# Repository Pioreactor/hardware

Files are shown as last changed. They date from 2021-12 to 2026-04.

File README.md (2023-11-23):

### HAT hardware setup

#### Installation

0. Install git: `sudo apt-get install git -y`
1. git clone this repo to your Raspberry Pi: `git clone --recurse-submodules https://github.com/Pioreactor/hardware.git && cd hardware`
2. Install eeprom utils: `cd hats/eepromutils && make && sudo make install && cd ..`
3. Move some files over: `mv ../eeprom/write_eeprom.py eepromutils/ && mv ../eeprom/pioreactor_eeprom_settings.txt.template eepromutils/`

#### Setting up a new HAT

0. Attach the HAT to the RPi.
1. Run `sudo bash setup_HAT.py`
2. Record the serial number/UUID
2. After a `sudo reboot`, try  `pio version -v` to confirm that HATs version.

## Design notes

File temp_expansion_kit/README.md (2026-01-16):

# Temperature Expansion Kit

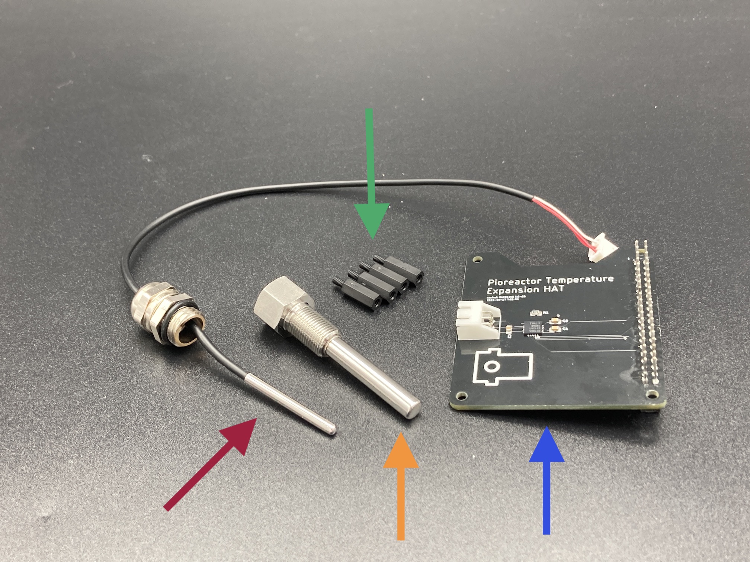
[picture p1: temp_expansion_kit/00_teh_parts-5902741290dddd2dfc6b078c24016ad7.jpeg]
Temperature Expansion Kit parts


### Pt1000 probe and cable

Need a 3-wire Pt1000 probe with jst connector. 

We Purchased from [here](https://www.alibaba.com/product-detail/GAIMC-Customized-waterproof-ClassA-PT1000-PT100_1600338752153.html?spm=a2756.trade-list-buyer.0.0.289276e9jdTwxA) 

 - 5mm diameter 47mm length hot sleeve with g1/8 threads
 - 3mm diameter probe

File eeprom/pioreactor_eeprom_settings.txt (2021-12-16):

########################################################################
# EEPROM settings text file
#
# Edit this file for your particular board and run through eepmake tool,
# then use eepflash tool to write to attached HAT ID EEPROM
#
# Tools available:
#  eepmake   Parses EEPROM text file and creates binary .eep file
#  eepdump   Dumps a binary .eep file as human readable text (for debug)
#  eepflash  Write or read .eep binary image to/from HAT EEPROM
#
########################################################################

########################################################################
# Vendor info

# 128 bit UUID. If left at zero eepmake tool will auto-generate
# RFC 4122 compliant UUID
product_uuid 00000000-0000-0000-0000-000000000000

# 16 bit product id
product_id 0x0001

# 16 bit product version
product_ver 0x0021

# ASCII vendor string  (max 255 characters)
vendor "Pioreactor Inc."

# ASCII product string (max 255 characters)
product "Pioreactor HAT"

# Custom binary data
2021-12-15T23:16:09.684411
########################################################################
# GPIO bank settings, set to nonzero to change from the default.
# NOTE these setting can only be set per BANK, uncommenting any of
# these will force the bank to use the custom setting.

# drive strength, 0=default, 1-8=2,4,6,8,10,12,14,16mA, 9-15=reserved
gpio_drive 0

# 0=default, 1=slew rate limiting, 2=no slew limiting, 3=reserved
gpio_slew 0

# 0=default, 1=hysteresis disabled, 2=hysteresis enabled, 3=reserved
gpio_hysteresis 0

# If board back-powers Pi via 5V GPIO header pins:
# 0 = board does not back-power
# 1 = board back-powers and can supply the Pi with a minimum of 1.3A
# 2 = board back-powers and can supply the Pi with a minimum of 2A
# 3 = reserved
# If back_power=2 then USB high current mode will be automatically
# enabled on the Pi
back_power 0

########################################################################
# GPIO pins, uncomment for GPIOs used on board
# Options for FUNCTION: INPUT, OUTPUT, ALT0-ALT5
# Options for PULL: DEFAULT, UP, DOWN, NONE
# NB GPIO0 and GPIO1 are reserved for ID EEPROM so cannot be set

#         GPIO  FUNCTION  PULL
#         ----  --------  ----
#setgpio  2     INPUT     DEFAULT
#setgpio  3     INPUT     DEFAULT
#setgpio  4     INPUT     DEFAULT
#setgpio  5     INPUT     DEFAULT
#setgpio  6     INPUT     DEFAULT
#setgpio  7     INPUT     DEFAULT
#setgpio  8     INPUT     DEFAULT
#setgpio  9     INPUT     DEFAULT
#setgpio  10    INPUT     DEFAULT
#setgpio  11    INPUT     DEFAULT
setgpio  12    OUTPUT     DEFAULT
setgpio  13    OUTPUT     DEFAULT
#setgpio  14    INPUT     DEFAULT
#setgpio  15    INPUT     DEFAULT
setgpio  16    OUTPUT     DEFAULT
setgpio  17    OUTPUT     DEFAULT
setgpio  18    OUTPUT     DEFAULT
#setgpio  19    INPUT     DEFAULT
#setgpio  20    INPUT     DEFAULT
#setgpio  21    INPUT     DEFAULT
#setgpio  22    INPUT     DEFAULT
setgpio  23    OUTPUT     DEFAULT
setgpio  24    INPUT     DEFAULT
setgpio  25    INPUT     DEFAULT
#setgpio  26    INPUT     DEFAULT
#setgpio  27    INPUT     DEFAULT

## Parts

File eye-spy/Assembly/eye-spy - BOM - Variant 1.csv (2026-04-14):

Reference | Qty | Description | Value | Manufacturer 1 | Manufacturer Part Number 1
C1 | 1 | CAP CER 10000PF 100V C0G 1206 | 10nF | Murata Electronics | GCM3195C2A103JA16D
C2,C4 | 2 | CAP CER 0.1UF 50V X7R 0402 | 0.1 uF | Murata Electronics | GRM155R71H104KE14J
C3 | 1 | CAP CER 1UF 50V X7R 1206 | 1uF | Murata Electronics | GRM31CR71H105KA61L
C5 | 1 | CAP TANT 10UF 10% 16V 1206 | 10uF | KYOCERA AVX | TAJA106K016RNJ
D1 | 1 | SENSOR PHOTODIODE 940NM 2SMD | VEMD2000X01 | Vishay Semiconductor | VEMD2000X01
D2,D3,D4,D5 | 4 | TVS DIODE 5V 15V SOD923 | DF2S6.8MFS,L3M | Toshiba | DF2S6.8MFS,L3M
J1,J2 | 2 | CONN HEADER SMD 4POS 1MM | BM04B-SRSS-TB | JST Sales America Inc. | BM04B-SRSS-TB
PCB1 | 1 | PCB | 3_20250920
R1 | 1 | RES 3.01M OHM 1% 1/16W 0402 | 3.01M | Yageo | RC0402FR-073M01L
R2,R4,R5,R6 | 4 | RES SMD 49.9 OHM 1% 1/16W 0402 | 49.9R | Yageo | RC0402FR-0749R9L
R3,R7 | 2 | RES 47K OHM 1% 1/16W 0402 | 47k | Yageo | RC0402FR-0747KL
U1 | 1 | IC OPAMP GP 1 CIRCUIT SC70-5 | TLV9101IDCK | Texas Instruments | TLV9101IDCK
U2 | 1 | IC ADC 16BIT SIGMA-DELTA 10VSSOP | ADS1114IDGS | Texas Instruments | ADS1114IDGSR

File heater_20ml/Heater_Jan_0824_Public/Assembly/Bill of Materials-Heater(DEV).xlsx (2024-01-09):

Designator | Value | Description | Manufacturer 1 | Manufacturer Part Number 1 | Supplier 1 | Supplier Part Number 1 | Supplier Unit Price 1 | Quantity | Supplier Subtotal 1
C1, C3 | 2.2uF | CAP CER 2.2UF 25V X5R 0603 | Murata | GRM188R61E225MA12D | Digi-Key | 490-12738-1-ND | 0.13 | 2 | 0.26
C2, C4 | 0.1uF | CAP CER 0.1UF 50V X7R 0402 | Murata | GRM155R71H104KE14J | Digi-Key | 490-13342-1-ND | 0.1 | 2 | 0.2
J1 | 0522070760 | CONN FFC FPC TOP 7POS 1.00MM R/A | Molex | 52207-0760 | Digi-Key | WM3818TR-ND |  | 1
MTL1, MTL2 | 9774030151R | RND STANDOFF M2.5X0.45 STEEL 3MM | Wurth Electronics | 9774030151R | Digi-Key | 732-7083-1-ND | 1.01 | 2 | 2.02
PCB1 | 4_20221023_001 |  |  |  |  |  |  | 1
R9 | 10k | RES SMD 10K OHM 1% 1/16W 0402 | Yageo | RC0402FR-0710KL | Digi-Key | 311-10.0KLRCT-ND | 0.1 | 1 | 0.1
R12, R13, R14, R16, R17, R19, R20, R21, R22, R23, R24, R25, R26, R27, R28 | 3.9R | RES SMD 3.9 OHM 5% 1/2W 1206 | Rohm | ESR18EZPJ3R9 | Digi-Key | RHM3.9ITR-ND |  | 15
U1 | TMP1075DSGR | IC TEMP SENSOR | Texas Instruments | TMP1075DSGR | Digi-Key | 296-TMP1075DSGRTR-ND |  | 1
U2 | DRV5021A3QDBZR | HALL EFFECT SENSOR | Texas Instruments | DRV5021A3QDBZR | Digi-Key | 296-DRV5021A3QDBZRCT-ND | 0.92 | 1 | 0.92

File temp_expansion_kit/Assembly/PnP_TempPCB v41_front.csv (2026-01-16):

Name | X | Y | Angle | Value | Package
C1 | 36.48 | 27.78 | 90.00 | 0.1uF | 0805-NO
C2 | 33.23 | 27.73 | 90.00 | 0.1uF | 0805-NO
C3 | 35.97 | 14.87 | 0.00 | 10nF | 0805-NO
R1 | 29.52 | 22.26 | 90.00 | 4300Ω 0.1% | 0805-NO
U1 | 36.04 | 21.68 | 270.00 | MAX31865 | QFN20_4MM_0.65MM

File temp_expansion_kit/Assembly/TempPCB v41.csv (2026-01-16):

Qty | Value | Device | Package | Parts | Description | CATEGORY | DESCRIPTION | MANUFACTURER | MPN | OPERATING_TEMPERATURE | PARTREV | PART_STATUS | PITCH | ROHS_COMPLIANCE | SERIES | STANDARD | SUBCATEGORY | TYPE
1 |  | SSQ-120-03-T-D | SAMTEC_SSQ-120-03-T-D | JP2 |  |  |  | Samtec Inc. |  |  | R |  |  |  |  | Manufacturer Recommendations
2 | 0.1uF | CAP_CERAMIC0805-NOOUTLINE | 0805-NO | C1, C2 | Ceramic Capacitors
1 | 10nF | CAP_CERAMIC0805-NOOUTLINE | 0805-NO | C3 | Ceramic Capacitors
1 | 3A/250V | S3B-XH-A | S3B-XH-A | J2 |  | Header | Connector Header Through Hole | (2.50mm) | JST Sales America Inc. | S3B-XH-A(LF)(SN) | -25°C ~ 85°C |  | Active | (2.50mm) | ROHS3 Compliant | XH |  | Rectangular Connectors
1 | 4300Ω 0.1% | RESISTOR0805_NOOUTLINE | 0805-NO | R1 | Resistors
1 | MAX31865 | TEMP_MAX31865 | QFN20_4MM_0.65MM | U1 | MAX31865 - Resistance to Digital Convertor for Platinum Resistance Temperature Detectors (RTDs)

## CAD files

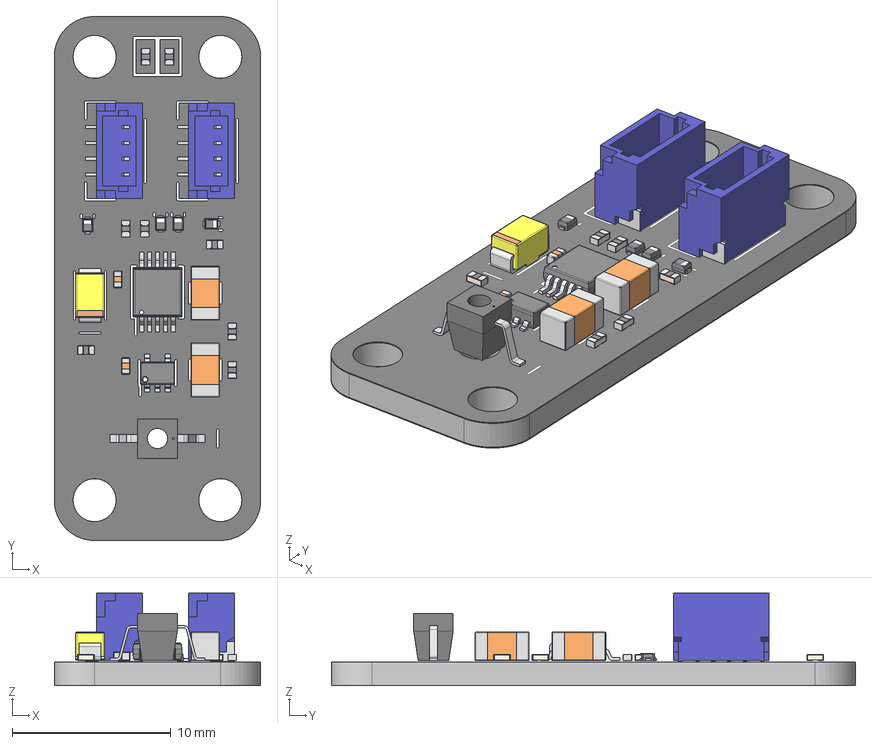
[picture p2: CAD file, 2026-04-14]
CAD/eye-spy.step
13.0 x 33.0 x 5.90 mm
JST_BM04B-SRSS-TB x 2
RESC100X50X40L25N x 8
CAPC320X160X180L55N x 2
SODFL100X60X45L17X30N x 4
CAPC100X50X55L25N x 2
CAPPM320X160X180L85X120N
SOP10P50_300X490X110L55X22N
VITEC_VEMD2000X01
SOP6-5P65_200X210X100L36X24N
eye-spy_silkscreen
eye-spy_soldermask
eye-spy_PCB

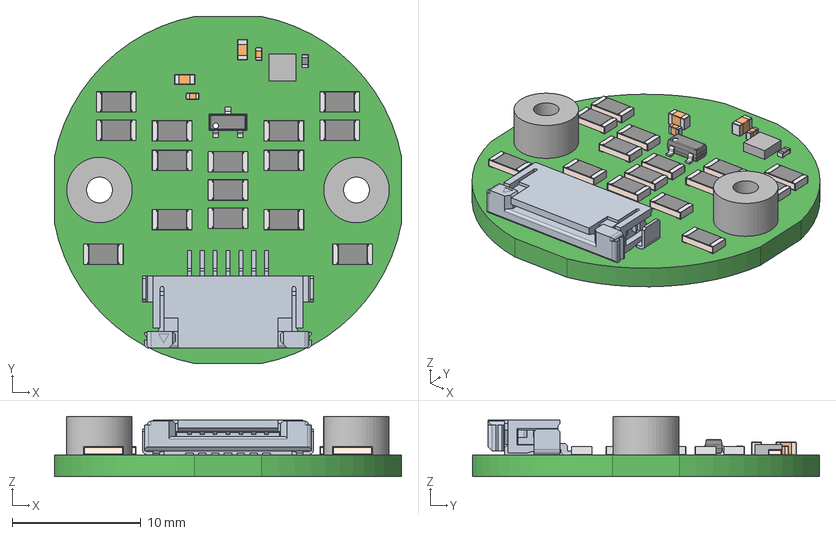
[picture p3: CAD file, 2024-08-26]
CAD/heater_20ml/heater_20ml_v1.0.step
27.0 x 27.0 x 4.70 mm
R_1206_0.55mm x 15
R_0402_0.55mm
Extruded
9774030151R (rev1)_RGB8421504 x 2
Q_NTR4101PT1G_1.11mm
C_0402_0.7mm x 2
C_0603_1.0mm x 2

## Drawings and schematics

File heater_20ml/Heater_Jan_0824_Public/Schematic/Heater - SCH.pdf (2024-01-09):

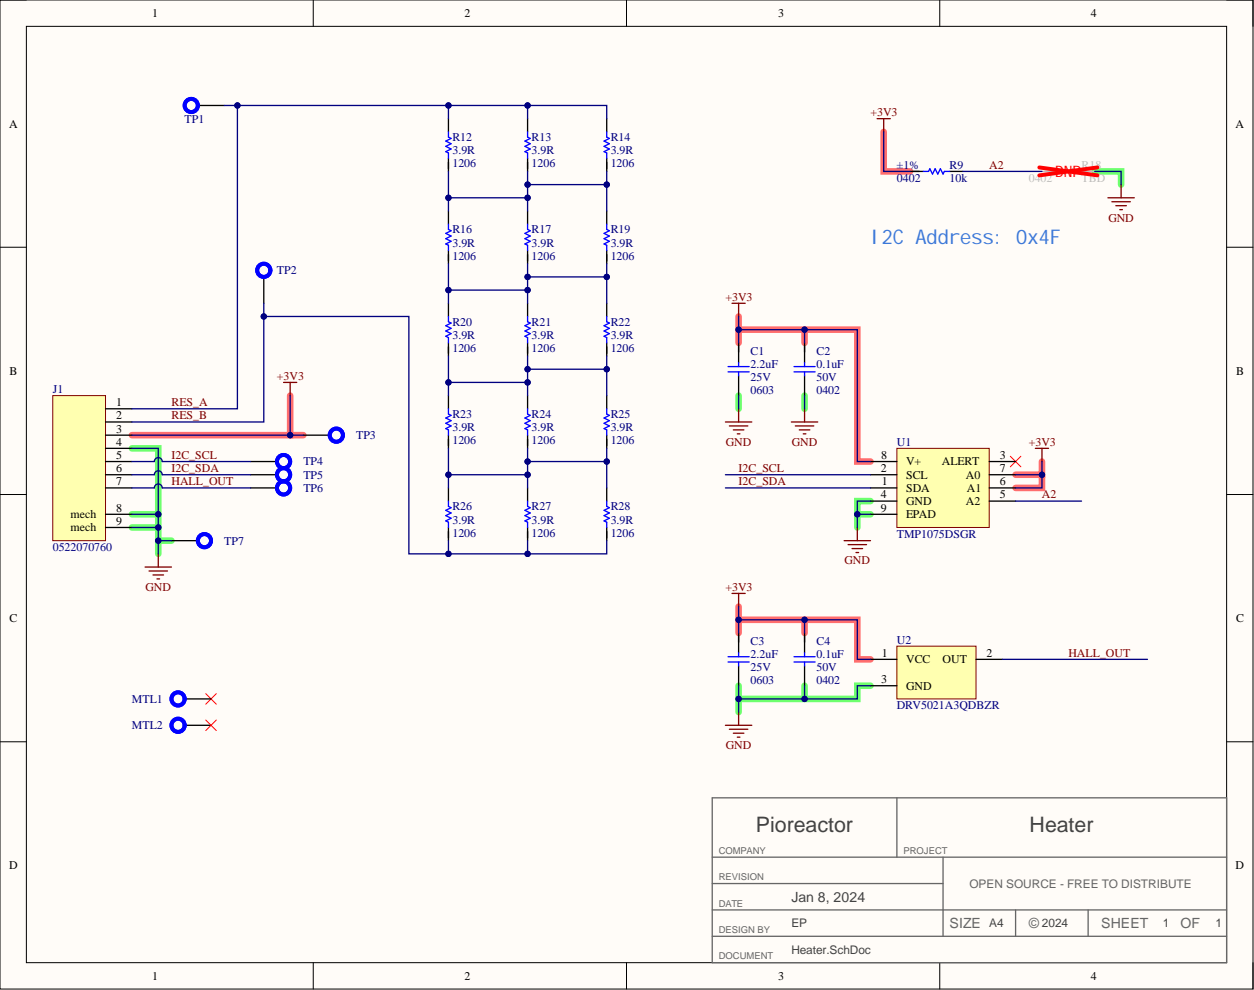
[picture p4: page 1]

Pioreactor COMPAN Y | Heater PRO JECT

REVISIO N | OPEN SOURCE - FREE TO DISTRIBUTE

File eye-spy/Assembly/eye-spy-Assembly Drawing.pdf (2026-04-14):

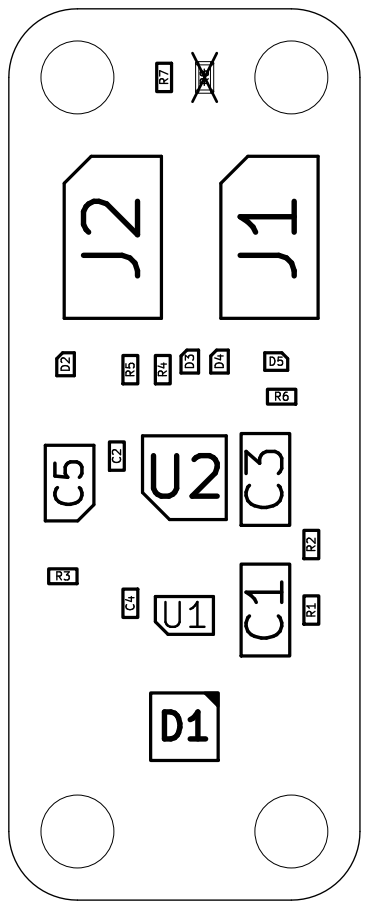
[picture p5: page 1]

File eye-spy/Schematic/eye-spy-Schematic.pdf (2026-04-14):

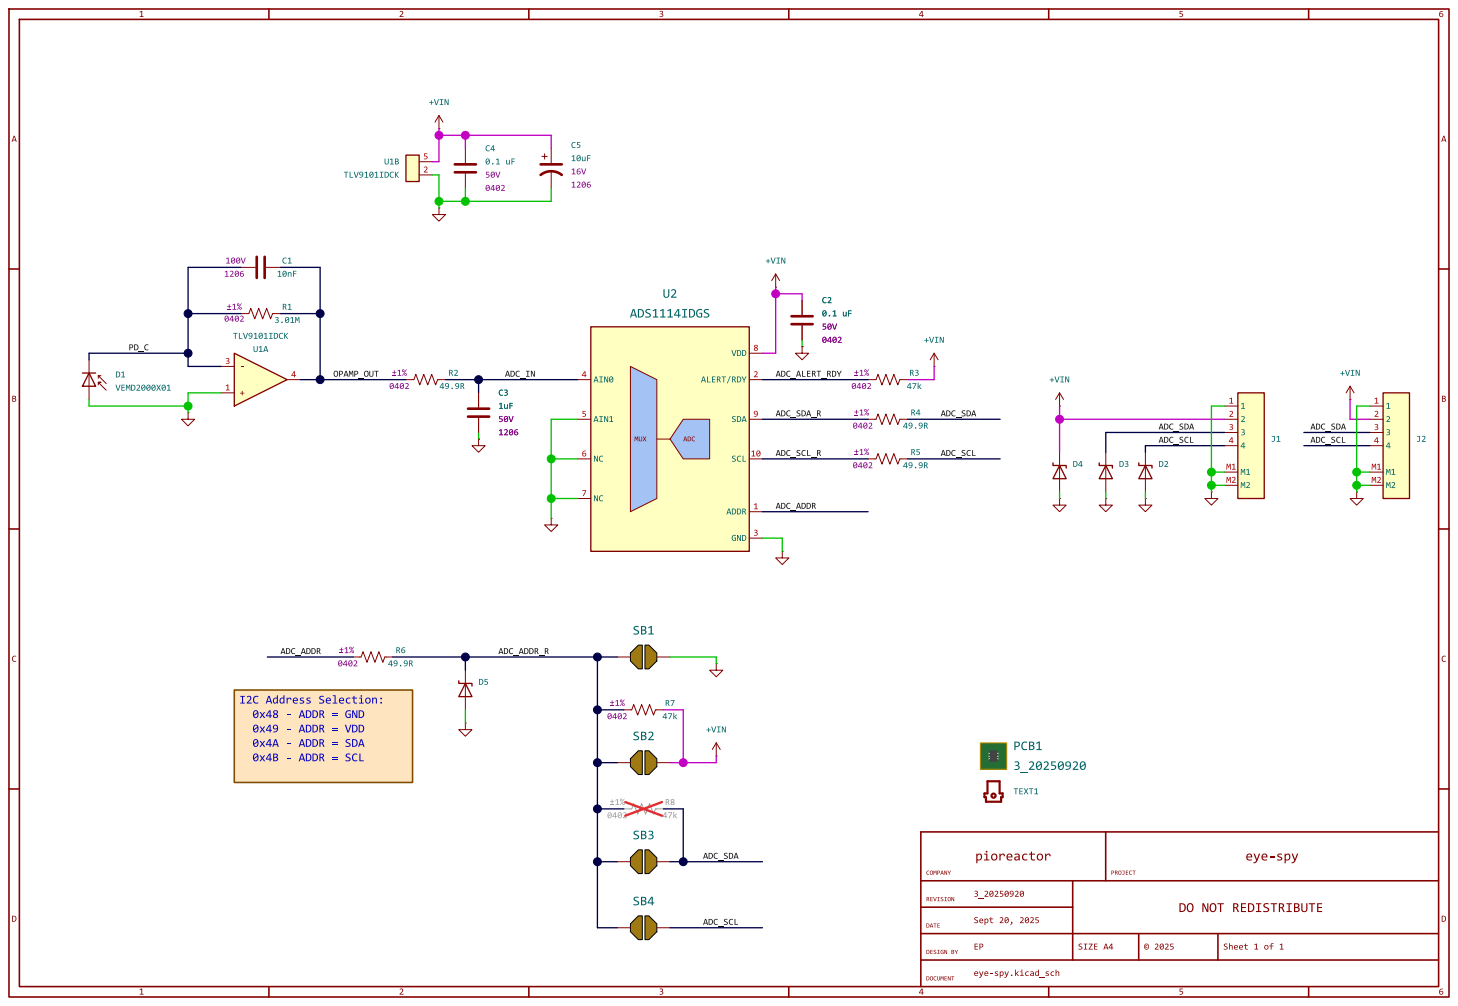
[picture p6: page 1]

Sheet 1 of 1 DO NOTREDISTRIBUTE

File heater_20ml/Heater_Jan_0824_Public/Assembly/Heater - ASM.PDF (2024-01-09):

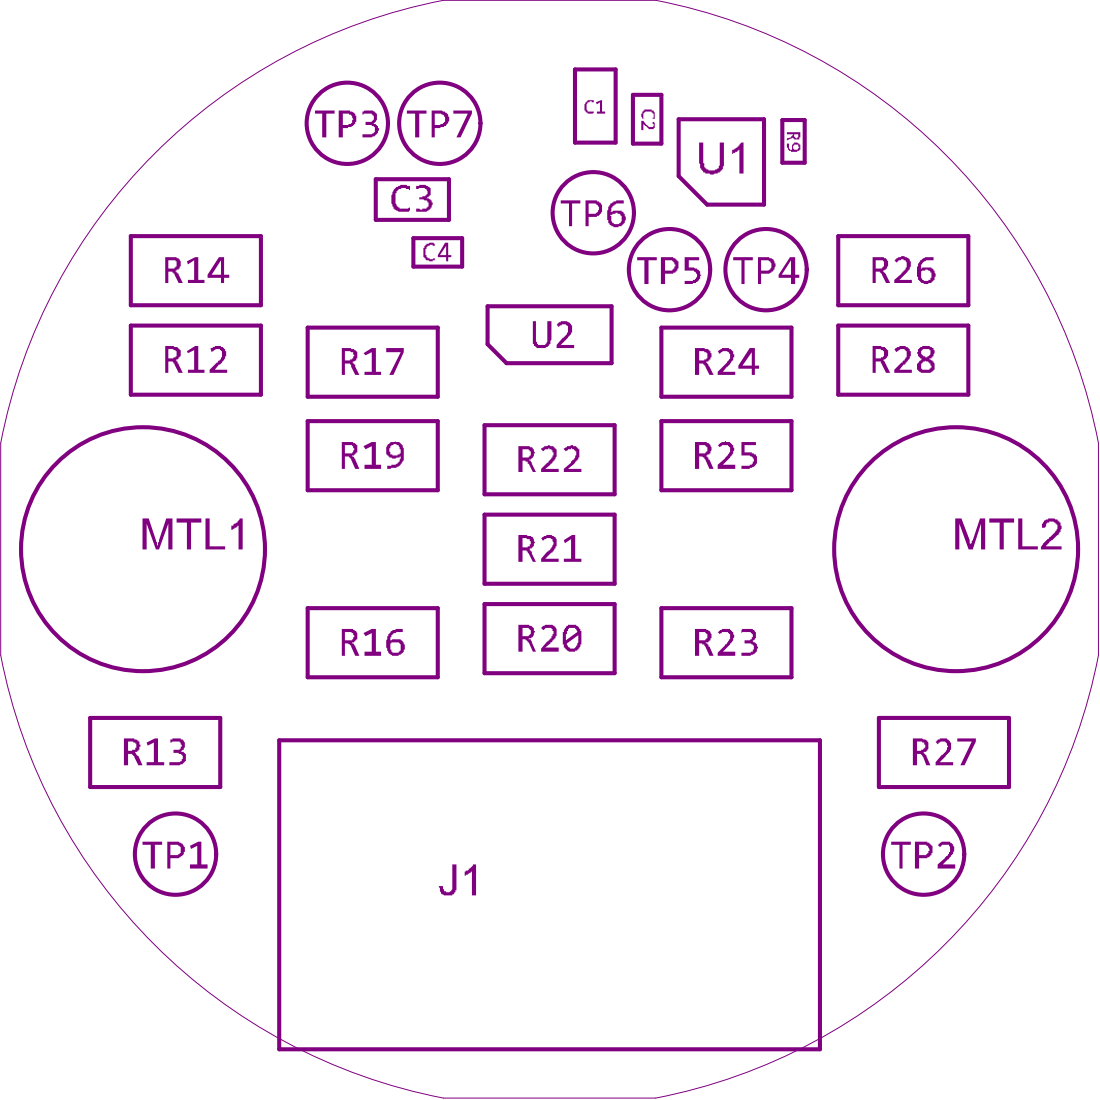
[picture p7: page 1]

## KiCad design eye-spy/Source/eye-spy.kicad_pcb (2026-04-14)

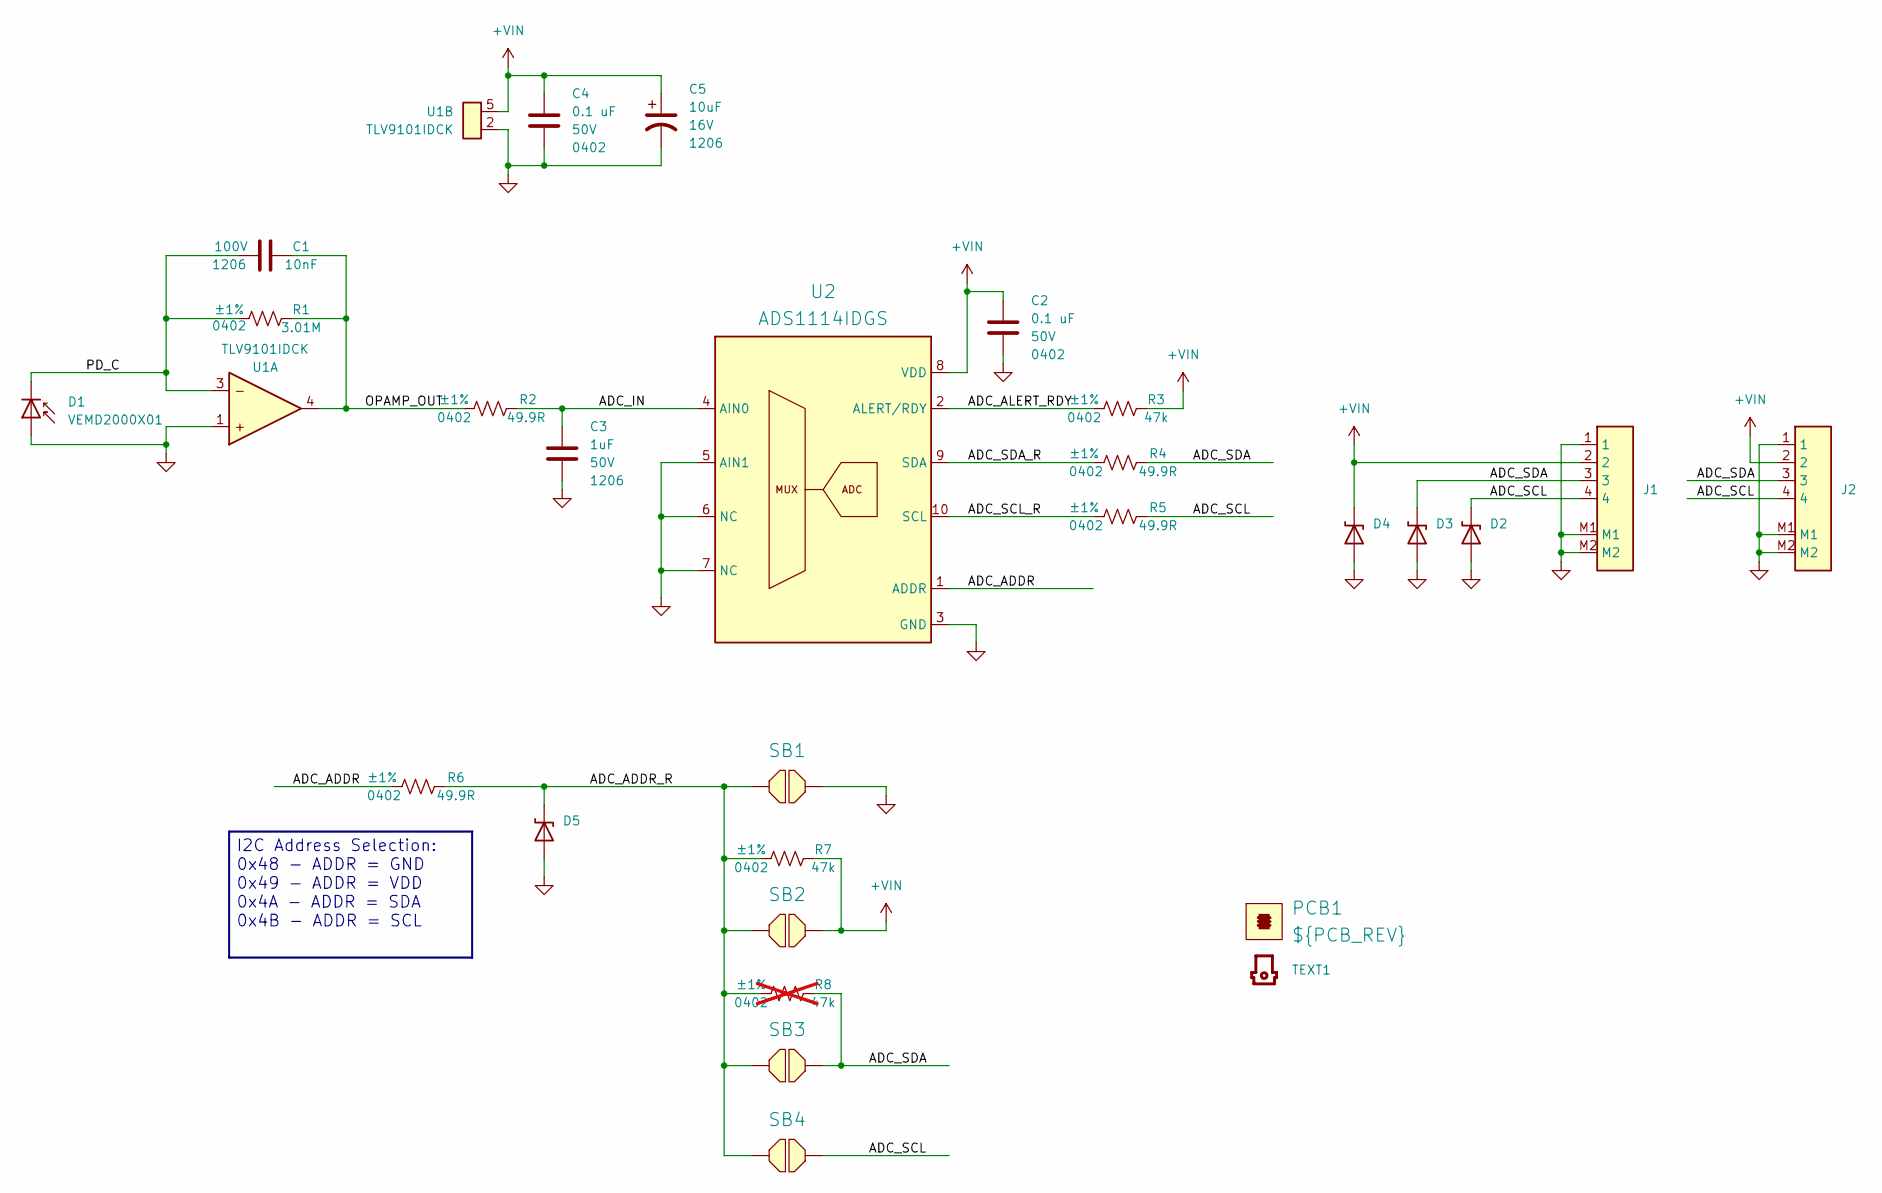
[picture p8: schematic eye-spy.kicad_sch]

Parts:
C1: 10nF; CAPC320X160X180L55N; Tolerance ±5%; Voltage 100V; Manufacturer Part Numbe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 GCM3195C2A103JA16D
C2, C4: 0.1 uF; CAPC100X50X55L25N; Tolerance ±10%; Voltage 50V; Manufacturer Part Numbe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 GRM155R71H104KE14J
C3: 1uF; CAPC320X160X180L55N; Tolerance ±10%; Voltage 50V; Manufacturer Part Numbe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 GRM31CR71H105KA61L
C5: 10uF; CAPPM320X160X180L85X120N; Tolerance ±10%; Voltage 16V; Manufacturer Part Numbe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 TAJA106K016RNJ
D1: VEMD2000X01; VITEC_VEMD2000X01; Manufacturer Part Numbe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 VEMD2000X01
D2, D3, D4, D5: DF2S6.8MFS,L3M; SODFL100X60X45L17X30N; Manufacturer Part Numbe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 DF2S6.8MFS,L3M
J1, J2: BM04B-SRSS-TB; JST_BM04B-SRSS-TB; Manufacturer Part Numbe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 BM04B-SRSS-TB
PCB1: ${PCB_REV}
R1: 3.01M; RESC100X50X40L25N; Tolerance ±1%; Manufacturer Part Numbe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 RC0402FR-073M01L
R2, R4, R5, R6: 49.9R; RESC100X50X40L25N; Tolerance ±1%; Manufacturer Part Numbe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 RC0402FR-0749R9L
R3, R7: 47k; RESC100X50X40L25N; Tolerance ±1%; Manufacturer Part Numbe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 RC0402FR-0747KL
R8: 47k; RESC100X50X40L25N; Tolerance ±1%; Manufacturer Part Numbe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 RC0402FR-0747KL; not fitted
SB1, SB2, SB3, SB4: R_0402_SB
TEXT1: logo
U1: TLV9101IDCK; SOP6-5P65_200X210X100L36X24N; Manufacturer Part Numbe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 TLV9101IDCK
U2: ADS1114IDGS; SOP10P50_300X490X110L55X22N; Manufacturer Part Numbe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 ADS1114IDGSR

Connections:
+VIN: C2.1, C4.1, C5.1, D4.1 (CATHODE), J1.2, J2.2, R3.2, R7.2, SB2.2, U1.5 (V+), U2.8 (VDD)
/ADC_ADDR: R6.1, U2.1 (ADDR)
/ADC_ADDR_R: D5.1 (CATHODE), R6.2, R7.1, R8.1, SB1.1, SB2.1, SB3.1, SB4.1
/ADC_ALERT_RDY: R3.1, U2.2 (ALERT/RDY)
/ADC_IN: C3.1, R2.2, U2.4 (AIN0)
/ADC_SCL: D2.1 (CATHODE), J1.4, J2.4, R5.2, SB4.2
/ADC_SCL_R: R5.1, U2.10 (SCL)
/ADC_SDA: D3.1 (CATHODE), J1.3, J2.3, R4.2, R8.2, SB3.2
/ADC_SDA_R: R4.1, U2.9 (SDA)
/OPAMP_OUT: C1.2, R1.2, R2.1, U1.4 (OUT)
/PD_C: C1.1, D1.1 (CATHODE), R1.1, U1.3 (IN-)
GND: C2.2, C3.2, C4.2, C5.2, D1.2 (ANODE), D2.2 (ANODE), D3.2 (ANODE), D4.2 (ANODE), D5.2 (ANODE), J1.1, J1.M1, J1.M2, J2.1, J2.M1, J2.M2, SB1.2, U1.1 (IN+), U1.2 (V-), U2.3 (GND), U2.5 (AIN1), U2.6 (NC), U2.7 (NC)

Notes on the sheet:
I2C Address Selection: 0x48 - ADDR = GND 0x49 - ADDR = VDD 0x4A - ADDR = SDA 0x4B - ADDR = SCL

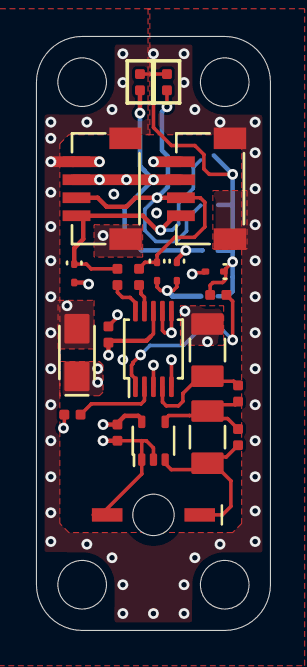
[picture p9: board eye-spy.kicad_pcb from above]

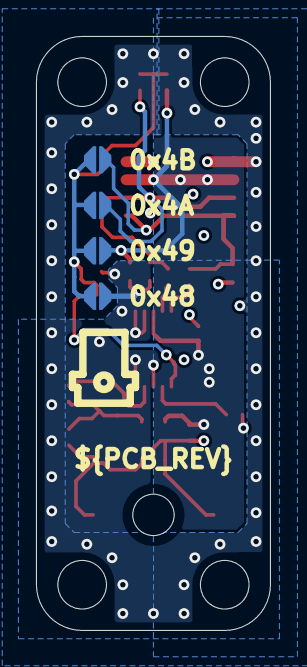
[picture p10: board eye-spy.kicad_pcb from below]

Board: 4 copper layers, 13.0 x 33.0 mm, 27 parts (5 on the bottom side), 12 nets.

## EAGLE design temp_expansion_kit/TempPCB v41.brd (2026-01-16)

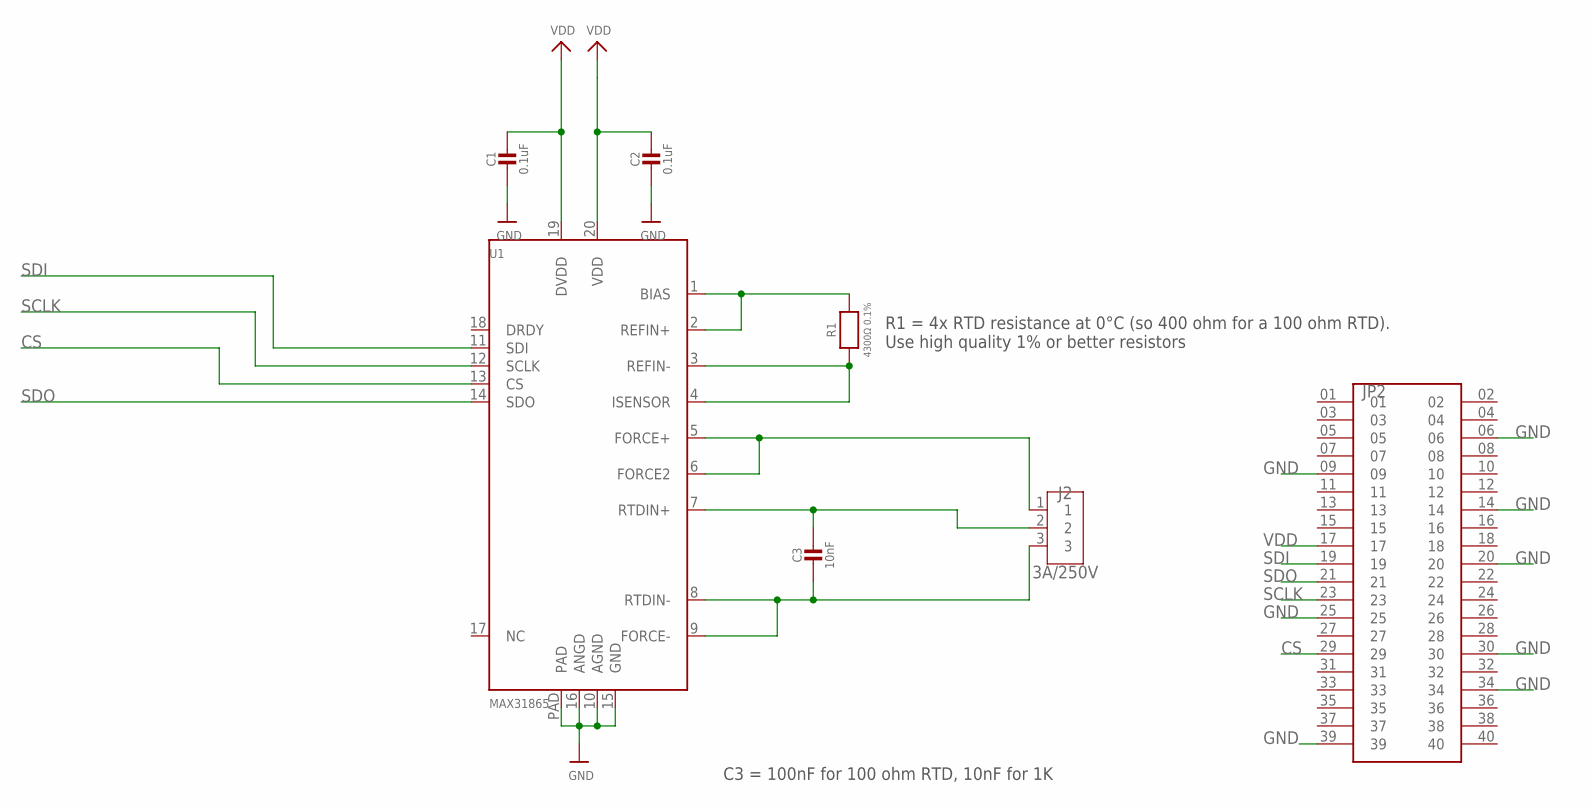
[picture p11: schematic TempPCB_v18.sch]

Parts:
C1, C2: 0.1uF; 0805-NO
C3: 10nF; 0805-NO
J2: 3A/250V; S3B-XH-A
JP2: SSQ-120-03-T-D; SAMTEC_SSQ-120-03-T-D
R1: 4300Ω 0.1%; 0805-NO
U1: MAX31865; QFN20_4MM_0.65MM

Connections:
CS: JP2.29, U1.13 (CS)
FORCE+: J2.1, U1.5 (FORCE+), U1.6 (FORCE2)
GND: C1.2, C2.2, JP2.06, JP2.09, JP2.14, JP2.20, JP2.25, JP2.30, JP2.34, JP2.39, U1.10 (AGND), U1.15 (GND), U1.16 (ANGD), U1.PAD
unnamed: R1.1, U1.3 (REFIN-), U1.4 (ISENSOR)
unnamed: R1.2, U1.1 (BIAS), U1.2 (REFIN+)
RTDIN+: C3.1, J2.2, U1.7 (RTDIN+)
RTDIN-: C3.2, J2.3, U1.8 (RTDIN-), U1.9 (FORCE-)
SCLK: JP2.23, U1.12 (SCLK)
SDI: JP2.19, U1.11 (SDI)
SDO: JP2.21, U1.14 (SDO)
VDD: C1.1, C2.1, JP2.17, U1.19 (DVDD), U1.20 (VDD)

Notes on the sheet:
C3 = 100nF for 100 ohm RTD, 10nF for 1K
R1 = 4x RTD resistance at 0°C (so 400 ohm for a 100 ohm RTD). Use high quality 1% or better resistors

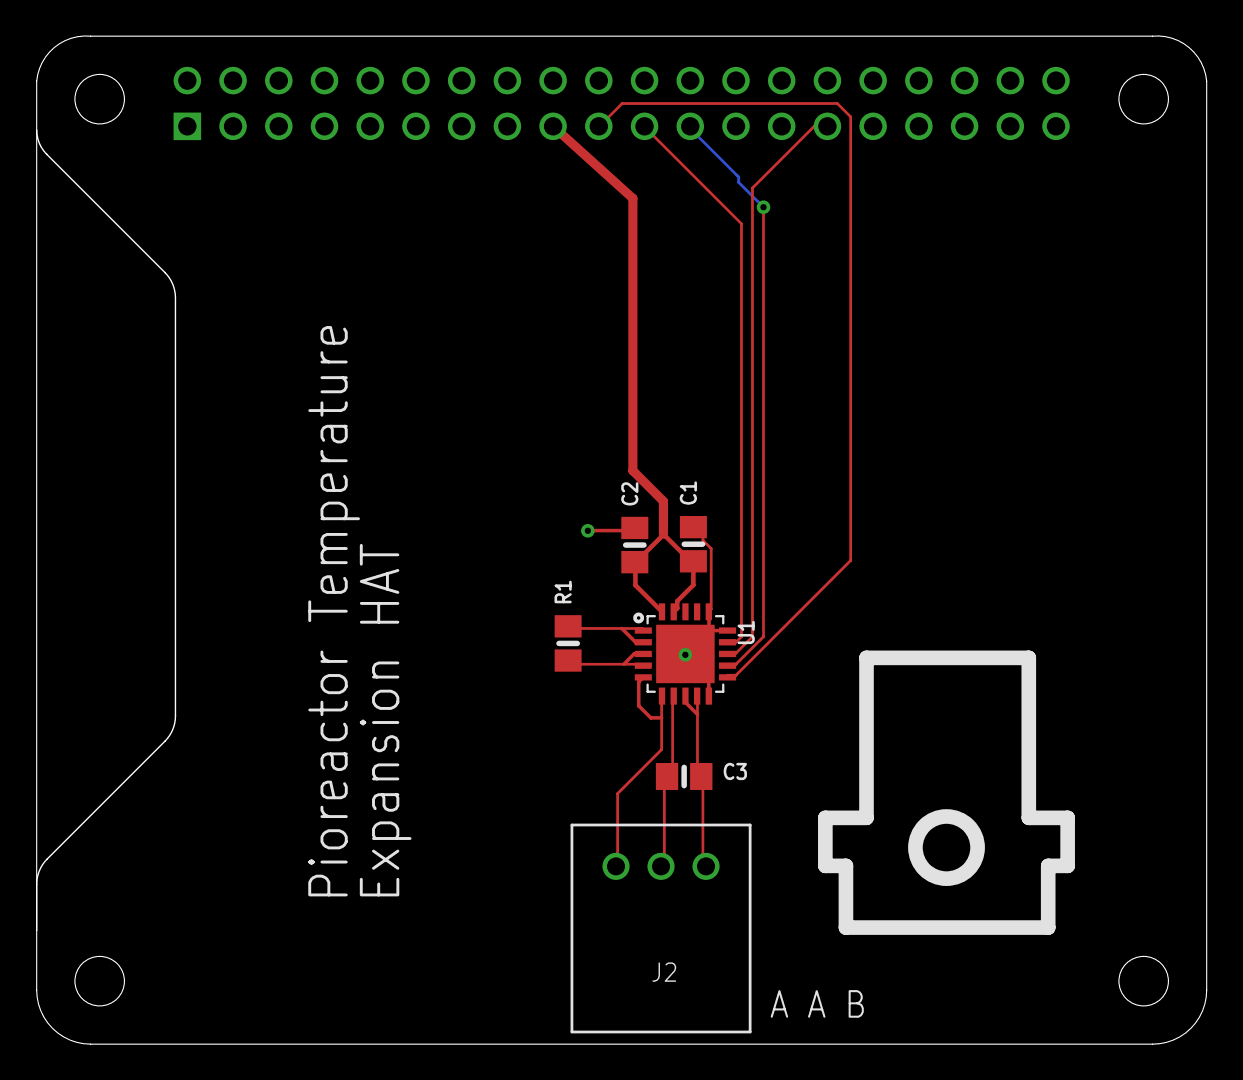
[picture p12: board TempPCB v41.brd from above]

Board: 2 copper layers, 65.0 x 56.0 mm, 7 parts (1 on the bottom side), 11 nets.

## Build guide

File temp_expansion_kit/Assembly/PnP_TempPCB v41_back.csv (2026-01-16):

Name | X | Y | Angle | Value | Package

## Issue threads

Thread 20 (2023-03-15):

### ISSUE TITLE
Pinout diagram of HAT

### ISSUE THREAD

**Issue by CamDavidsonPilon** [Pioreactor/hardware#20]
https://github.com/j0ono0/pinout

https://github.com/yaqwsx/PcbDraw

**Comment by VitorFrost** [comment]
Can you post here at list the circuit diagram? anything? 
I just want to understand a little more how things are connected, and what sensors are used.
I do believe I am using a different temperature sensor. I also would like to know what port is controlling the leds.

**Comment by VitorFrost** [comment]
Thanks for the info, that is enough for me.  I am using the `pin 4` for 1-wire communication, to connect a temperature sensor (Dallas DS16B20).
I have chosen it because I am housing the sensor inside an straw tube, that is inserted in the reactor! So I restricted the sensor to the encapsulation TO-92, to be digital and works with 3,3V .

**Comment by CamDavidsonPilon** [comment]
> I have chosen it because I am housing the sensor inside an stainless straw tube, that is inserted in the reactor

That's a cool idea!

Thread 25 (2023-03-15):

### ISSUE TITLE
use ads1015

### ISSUE THREAD

**Issue by CamDavidsonPilon** [Pioreactor/hardware#25]

**Comment by VitorFrost** [comment]
I am planning to use this to read an ADS1115 to read an pH sensor for Arduino.
Do you have any suggestion where to start it?

**Comment by VitorFrost** [comment]
Does this helps you?
https://github.com/msurguy/processing-mqtt-sensor-demo

**Comment by CamDavidsonPilon** [comment]
Our current development HATs use the ADS1115, but we plan to use 1015 for production. 

> I am planning to use this to read an ADS1115 to read an pH sensor for Arduino.

Is it correct that `Raspberry Pi <-> Arduino <-> ADS1115`? What is the purpose of the Arduino? 

Currently there aren't any Arduino tools in Pioreactor.

**Comment by VitorFrost** [comment]
> Our current development HATs use the ADS1115, but we plan to use 1015 for production.
> 
> > I am planning to use this to read an ADS1115 to read an pH sensor for Arduino.
> 
> Is it correct that `Raspberry Pi <-> Arduino <-> ADS1115`? What is the purpose of the Arduino?
> 
> Currently there aren't any Arduino tools in Pioreactor.

Actually, no. I am planning to use this sensor/module : https://www.e-tinkers.com/2019/11/measure-ph-with-a-low-cost-arduino-ph-sensor-board/
There are 3,3V of it, but they are very rare and _expensiver_ . 
I am planning to use like this:
`Raspberry Pi <-> Logic level shifter <-> ADS1x15`

**Comment by VitorFrost** [comment]
Actually, pH sensing can be a must for bioreactors! Sometimes, it is more precise to control growth media addition by pH level, then by turbidimetry.

**Comment by CamDavidsonPilon** [comment]
Your setup makes sense to me. And it's over i2c, so like:

```
             i2c                     i2c      voltage
Raspberry Pi <-> Logic level shifter <-> ADS1x15 <- pH Sensor
```


Here's a really quick sketch of what the Pioreactor software might look like to read from the ADS1115:

```python
# -*- coding: utf-8 -*-
# filename: ~/.pioreactor/plugins/sense_ph.py
import click

from pioreactor.whoami import get_unit_name, get_latest_experiment_name
from pioreactor.config import config
from pioreactor.background_jobs.base import BackgroundJob
from pioreactor.utils import local_persistant_storage
from pioreactor.utils.timing import RepeatedTimer
from pioreactor.hardware import SCL, SDA

from adafruit_ads1x15.analog_in import AnalogIn 
from adafruit_ads1x15.ads1115 import ADS1115 as ADS
from busio import I2C 


class PHSensor(BackgroundJob):

    published_settings = {
        "pH": {"datatype": "float", "settable": False},
    }

    def __init__(self, sample_rate, unit, experiment):

        self.ads = ADS(I2C(SCL, SDA), data_rate=128, gain=1)
        self.analog_in = AnalogIn(self.ads, 0)
        self.pH = None

        self.read_ph_timer = RepeatedTimer(
            interval=1/sample_rate, # convert to seconds
            function=self.read_ph,
            run_immediately=True,
        ).start()

    def read_ph(self):
        raw = self.analog_in.voltage

        with local_persistant_storage("ph_calibration") as cache:
            # this published to MQTT
            self.pH = raw_to_calibrated(raw, cache) #raw_to_calibrated to be defined... 

    def on_ready_to_sleeping(self) -> None:
        self.read_ph_timer.pause()

    def on_sleeping_to_ready(self) -> None:
        self.read_ph_timer.unpause()

    def on_disconnect(self) -> None:
        self.read_ph_timer.cancel()


@click.command(name="sense_ph")
def click_sense_ph():
    """
    Start the pH sensor
    """

    job = PHSensor(
        sample_rate=config.getfloat(),
        unit=get_unit_name(),
        experiment=get_latest_experiment_name(),
    )
    job.block_until_disconnected()

```

and it can be run with `pio run sense_ph`

**Comment by VitorFrost** [comment]
Thanks for the file `sense_ph.py`
Just to clarify, if I am doing it wright:
I need to put this file in the folder `/home/pi/.pioreactor/plugins`
then run the command `pio run sense_ph` ?
Tried it, and got the error (tried to reboot it too):
```
pi@pioreactor:~ $ pio run sense_ph
Usage: pio run [OPTIONS] COMMAND [ARGS]...
Try 'pio run --help' for help.

Error: No such command 'sense_ph'.
```

Should the Web interface show anything? My `/plugins` page was empty too:
![image](https://user-images.githubusercontent.com/5491480/151254373-e7eb7cf0-92e7-4c69-b07a-ac4d13d0b4d5.png)

I have also installed de pip adafruit-ads1x15 library (https://learn.adafruit.com/raspberry-pi-analog-to-digital-converters/ads1015-slash-ads1115) and it worked fine.

Then I tried: 
```
pio update --app
pio update --ui
```
NOTE:  not able to do just` pio update`, it asked me what to update.

Nothing YET. Then, after another reboot, It showed on the Web UI, and also on the pio list-plugins.
Beside this, when I try to run `pio run sense_ph` got:
```
Usage: pio run [OPTIONS] COMMAND [ARGS]...
Try 'pio run --help' for help.

Error: No such command 'sense_ph'.
```
And the webpage plugin link points to `/Unknown` (Can a plugin point to other pages outside pioreacors default plugins?)
![image](https://user-images.githubusercontent.com/5491480/151256228-a174f075-3503-447a-8db7-073b1247d5a3.png)

Any suggestion? Is the problem related to not having a proper Pioreactor HAT? If so, can I bypass any HAT self-check?

**Comment by CamDavidsonPilon** [comment]
I don't think it's HAT related. 

Hm, you shouldn't need to reboot so often. Things should "just work". If you run `pio run --help`, what shows up? I'm guessing:
```
Usage: pio run [OPTIONS] COMMAND [ARGS]...

Options:
  --help  Show this message and exit.

Commands:
  backup_database         (leader only) Backup db to workers.
  export_experiment_data  (leader only) Export tables from db.

```

If so, it's because your Pioreactor isn't set as a worker. 

----

Ah! Looking back, this is an issue with first_boot again! I actually didn't give you the full list commands to run in [my comment here](https://github.com/Pioreactor/pioreactor/issues/238#issuecomment-1018824136). 

You'll need to run the rest: 
```
touch ~/home/pi/config_$(hostname).ini
printf "# Any settings here are specific to $(hostname), and override the settings in config.ini\n\n" >> /home/pi/.pioreactor/config_$(hostname).ini
cp ~/home/pi/config_$(hostname).ini $PIO_DIR/unit_config.ini
crudini --set ~/home/pi/config.ini network.inventory $(hostname) 1
```

The above edits your configuration file to make your Pioreactor a worker - _then_ you should be able to run `pio run sense_ph`. 


----

The script I gave you is just a demo, but there were a few silly bugs in it. Try [this updated version](https://gist.github.com/CamDavidsonPilon/e6c805593d718e0297641d8e47d903c0), plus that provides some metadata so information on the /plugins page is filled in.

**Comment by VitorFrost** [comment]
@CamDavidsonPilon Thanks for the diagnosis!
Yes, you was wright about `pio run --help`
But the command above has an error! you have added a `~/home/pi/` where should be only `~/`
I got this kind of error:
```
$ touch ~/home/pi/config_$(hostname).ini
touch: cannot touch '/home/pi/home/pi/config_pioreactor.ini': No such file or directory

```

Now I can finally see the reactor on the page `/pioreactors`
![image](https://user-images.githubusercontent.com/5491480/151381573-d6636c3c-acdc-49d6-80aa-0d69d7cda0ac.png)

And only after a reboot I was able to run `pio run sense_ph`
Thanks a lot for the work on the pH sensor!
Now I have to figure out how to proper program in python and fix the `name 'raw_to_calibrated' is not defined`  LOL

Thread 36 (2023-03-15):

### ISSUE TITLE
fiducials? 

### ISSUE THREAD

**Issue by CamDavidsonPilon** [Pioreactor/hardware#36]
What’s a fiducial and what’s it doing there on my PCB?

**Comment by repollo** [comment]
Fiducials are used as reference points/markers in pick-and-place machines for precise component placement, this is used a lot in Surface Mount Technology. Otherwise computers would have a hard time trying to install an SMD component on a PCB.

**Comment by CamDavidsonPilon** [comment]
:) thanks @repollo

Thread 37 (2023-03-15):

### ISSUE TITLE
Blue and white LEDs emitting some light even when driver is set to 0

### ISSUE THREAD

**Issue by CamDavidsonPilon** [Pioreactor/hardware#37]

**Comment by VitorFrost** [comment]
did you read it with an oscilloscope?
this happens always, or this happens when something else is on? This is common with interference from motors or even wi-fi.

**Comment by CamDavidsonPilon** [comment]
I haven't read it with an oscilloscope. It seems to be something with our LED driver circuit. There's no problem with red / IR leds, but there is with higher frequency LEDs - probably something to do with the forward voltage of them.

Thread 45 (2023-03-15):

### ISSUE TITLE
Agitation fan overheating for high viscosity medium?

### ISSUE THREAD

**Issue by VitorFrost** [Pioreactor/hardware#45]
Ok, I have tried to build an magnetic stirrer with 12V fan, but I got a fast overheating of the fan, specially with higher viscosity medium.
Had you monitored it? 
Had you tried it with high sugar concentration medium?
Some cells form filaments/blobs, that also creates trouble for bioreactors.

**Comment by CamDavidsonPilon** [comment]
I've had no problems with up to a 10% YPD mix (not _very_ viscous), and moving ~20ml. Your volume is much more, though, right? 

The software is agnostic to the voltage of motor. The default `stirring` job that we use just controls the DC% of a PWM signal applied to the motor. (The pioreactor hardware supports an auxiliary power supply of up to 18V, but by default it's 5v). 

For moving high viscosity, high volumes, you may need to upgrade to a brushed motor, but the same logic applies (control stirring speed via a PWM signal). 

> Some cells form filaments/blobs, that also creates trouble for bioreactors.

Like biofilms? Yea, always a concern. I haven't had much trouble with biofilms (yet) though.

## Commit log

2020-12-12 adding 3d files
    [Base.stl, Cap.stl, Holder v4.stl]
2020-12-13 new holder with 8 angles
    [Holder.stl]
2020-12-14 shorter base
    [Base.stl]
2022-08-22 remove these; not using them anymore
    [Base.step, Base.stl, Cap.stl, Holder.step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]
2023-11-02 turn off leds after test
2024-01-09 adding heater for 20ml pioreactor
    [Bill of Materials-Heater(DEV).xlsx, Heater.GM1, Heater.GTL, Heater.GTO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]
2024-07-29 adding assembly docs
    [Bill of Materials-Heater(DEV).xlsx, Pick Place for Heater(DEV).csv]
2024-08-26 STEP files of hardware
    [heater_20ml_v1.0.step]
2026-01-16 open source the temp hat
    [PnP_TempPCB v41_back.csv, PnP_TempPCB v41_front.csv, TempPCB v41.brd, TempPCB v41.csv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]
2026-04-15 step for eye-spy
    [eye-spy.step]

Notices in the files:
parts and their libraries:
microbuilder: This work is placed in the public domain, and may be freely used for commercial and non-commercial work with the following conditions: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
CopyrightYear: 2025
